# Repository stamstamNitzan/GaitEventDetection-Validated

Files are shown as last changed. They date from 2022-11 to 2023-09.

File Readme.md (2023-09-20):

# Gait Event Detection Device -> Validated

## Background
The gait events detection algorithm is based on angular velocity data from a single gyroscope mounted on the shank. The code was written for ***Arduino Nano 33 BLE Sense***. The developed device is part of a research study on the effect of haptic feedback on walking biomechanics parameters. With the algorithm, we can detect ***heel-strike*** and ***mid-swing events*** with ***high accuracy*** and provide gait event-dependent ***biofeedback***. 

The device was designed to be versatile and can be ***easily modified for other applications*** that could benefit from ***real-time gait event detection***, ***gait event-dependent feedback***, and ***gait data collection***. Angular velocity data can be collected with a nearby phone via BLE. The device is not confined to the lab setting. It can be modulated for other applications by adding sensors and functions, such as surface electromyography for muscle function monitoring, auditory and visual for biofeedback, and exoskeleton control for assistive walking.

We have validated the gait event detection algorithm's accuracy at detecting heel-strike. We have evaluated healthy participants' changes in ankle flexion moment and flexion angle when intermittent vibration is applied to the lower leg.

The accuracy of the gait event detection algorithm was validated against gold standard floor-embedded force plates (model BMS400600, AMTI, MA, USA). We compared the time difference between detecting a heel-strike event by the force plates and the device. The detection of heel-strike events in real-time by the device showed excellent agreement with the force plates at all three speeds (ICC = 1). Our device's mean difference and standard deviation in heel-strike detection are 19 ± 22 ms, and the sampling rate was 100 Hz. 

## Table of Contents
- [Background](#background)
- [Using the code for event-dependent processes and gait analysis](#using-the-code-for-event-dependent-processes-and-gait-analysis)
  * [Controlling the device via the nRF Connect app](#controlling-the-device-via-the-nrf-connect-app) 
  * [Algorithm workflow](#algorithm-workflow)
  * [Modifying the biofeedback](#modifying-the-biofeedback)
- [Device design and electrical diagram](#device-design-and-electrical-diagram)
  * [Electrical diagram](#electrical-diagram)
  * [Gait event detection validation](#gait-event-detection-validation)
  * [Gait dependent biofeedback](#gait-dependent-biofeedback)
- [License](#license)
- [Citation](#citation)
- [Contact](#contact)

## Using the code for event-dependent processes and gait analysis

The algorithm detects two gait events (heel-strike and mid-swing); however, accuracy measurements were done for heel-strike events. Our application was to use heel-strike events detection to activate intermittent vibration during specific parts of the stance phase. The code can be modified to provide any event-based processes that are in the scope of Arduino's abilities. 

We have uploaded three examples to this repository of using the algorithm. You can also find two ways to convert the recorded data from nRF Connect to meaningful angular velocity values. The first option is MATLAB code that does that automatically, and the second option is with Excel. All examples record the gyroscope's data to a buffer that can be sent to the phone at the end of each run. Only the `GaitDetectionOnlyRecordingGyro.ino` example is sending the data in real time.

Here are the examples:
- [GaitDetectionOnlyRecordingGyro.ino](GaitDetectionOnlyRecordingGyro/GaitDetectionOnlyRecordingGyro.ino) – sending gyroscope data to nRF Connect in real-time.
- [GaitDetectionLightOnly.ino](GaitDetectionLightOnly/GaitDetectionLightOnly.ino) – turning on LED on heel-strike events and turning it off on calculated toe-off events.
- [GaitDetectionWithVibration.ino](GaitDetectionWithVibration/GaitDetectionWithVibration.ino) – turning on the first vibration motor at heel-strike and turning on the second motor at about 30% of the gait cycle. Both motors are turned off at toe-off events (about 60% of the gait cycle).
- [DataConversionXMLtoMatlab.m](Post-analysis/DataConversionXMLtoMatlab.m) – import recorded XML files and converts the data to angular velocity meaningful values using MATLAB.
- [GyroDataExcelTutorial.pdf](Post-analysis/GyroDataExcelTutorial.pdf) – you can also use Excel to convert angular velocity to meaningful values. Explanation on how to convert gyro data from XML file to Excel by Omri Yosfan (omri.yy@gmail.com).

### Controlling the device via the nRF Connect app
After uploading the code to the Arduino Nano 33 BLE Sense, the device will be in standby mode, waiting for Bluetooth connection and commands. There are three commands:

`01` – "Reset", reset buffer

`02` – "Record", run the gait detection algorithm, send real-time gyroscope data, and/or provide event-dependent processes (when applicable).

`03` – "Replay", resend gyroscope data.

When sending the command "02", the code will run for the amount of time set by ` #define RECORDING_LENGTH_SECONDS `.

####  Working with the nRF Connect app 

**Step 1:** Download and install the app from your phone app store and give the required permissions. [https://www.nordicsemi.com/Products/Development-tools/nrf-connect-for-mobile](https://www.nordicsemi.com/Products/Development-tools/nrf-connect-for-mobile )

**Step 2:** Open the app and turn on Bluetooth and location access. Click on the scan button and connect to your device (the default is "Nitzan Arduino").

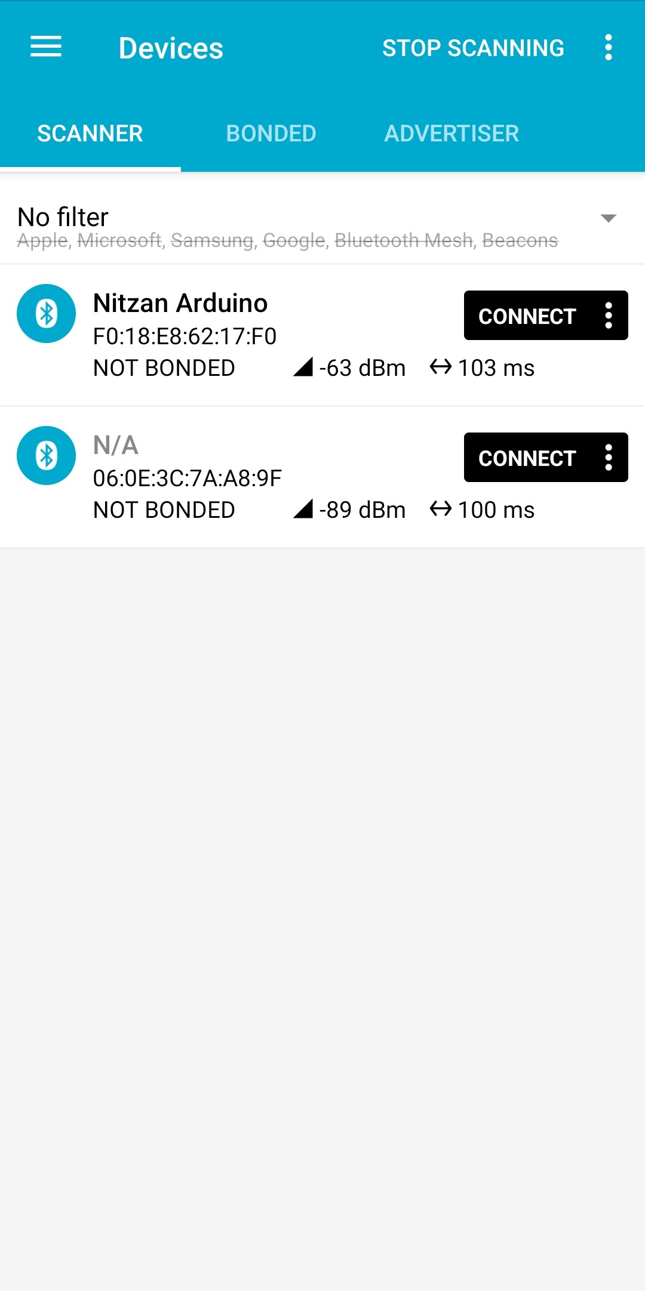
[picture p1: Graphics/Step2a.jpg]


**Step 3:** Press on the three dots next to "SERVER", click on "Request connection priority" and choose "HIGH".

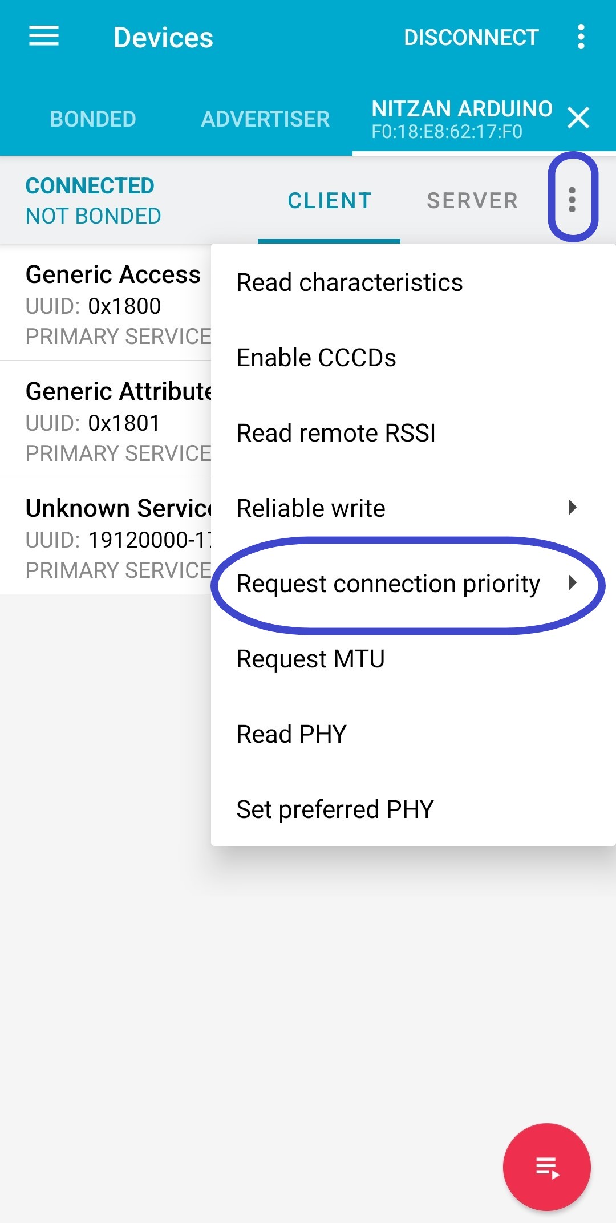
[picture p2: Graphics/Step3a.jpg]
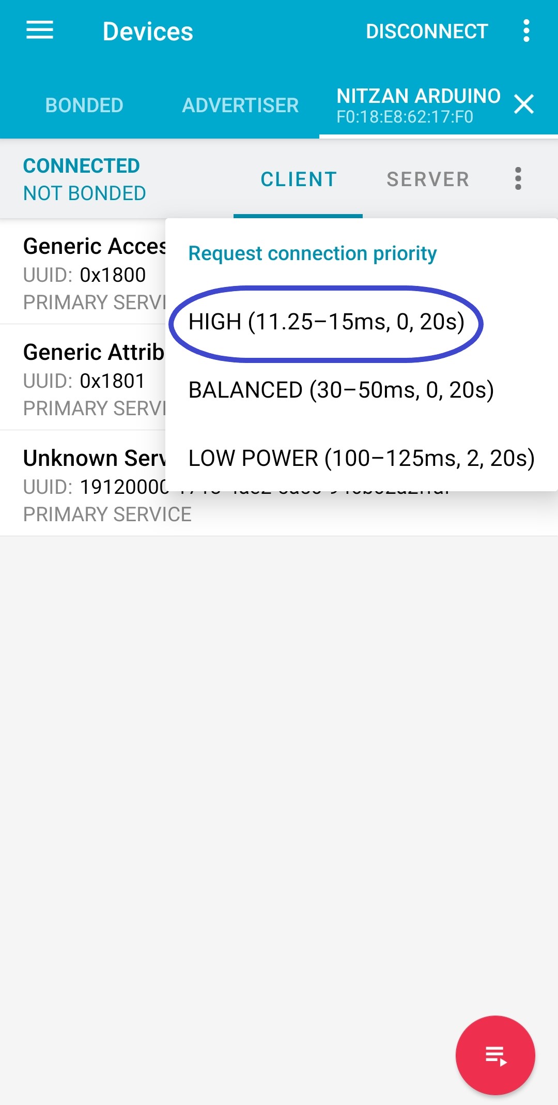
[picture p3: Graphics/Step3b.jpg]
        

**Step 4:** Press on "Unknown Service" and then press on the three arrows pointing down next to "Unknown Characteristic", this will let you receive the data from the Arduino.

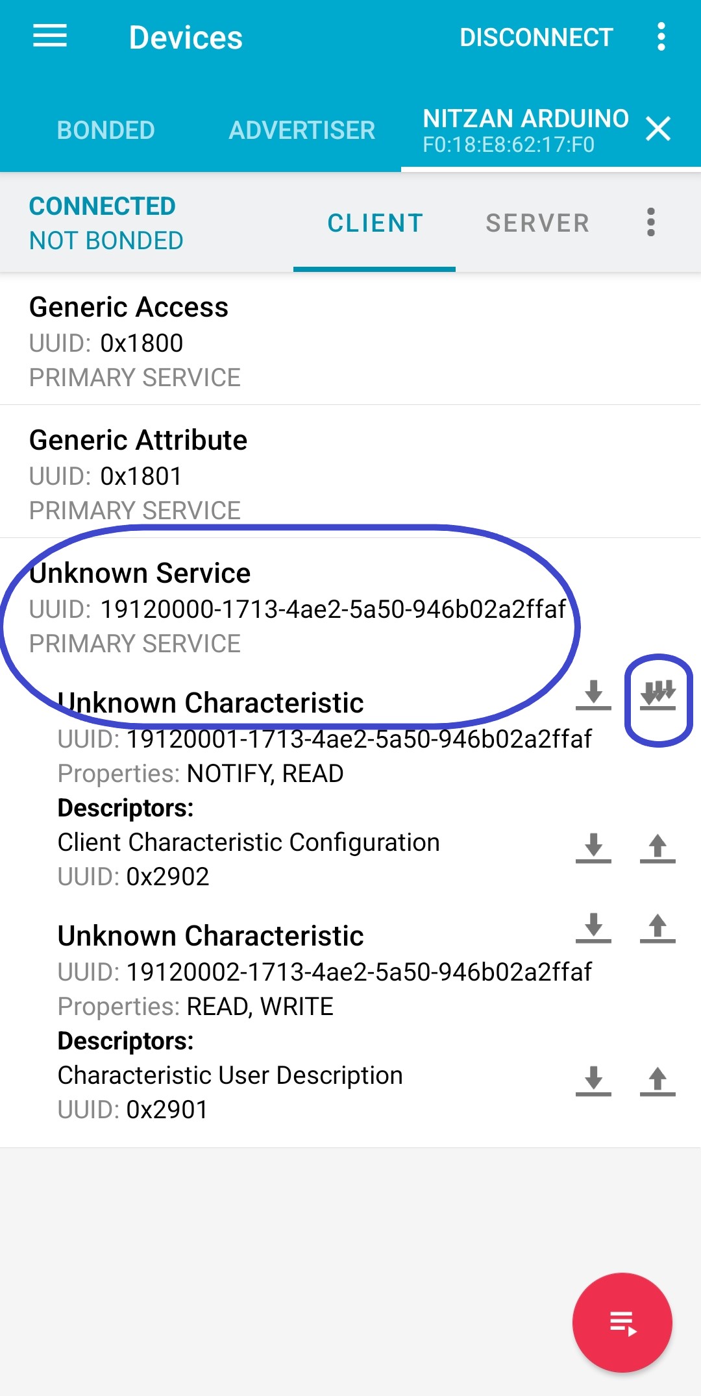
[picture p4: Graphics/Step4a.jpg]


**Step 5:** SENDING COMMANDS. As mentioned above, there are three commands, each with a corresponding number. Press on the middle arrow pointing UP to open the command dialog. Press "SEND" to commit the command.

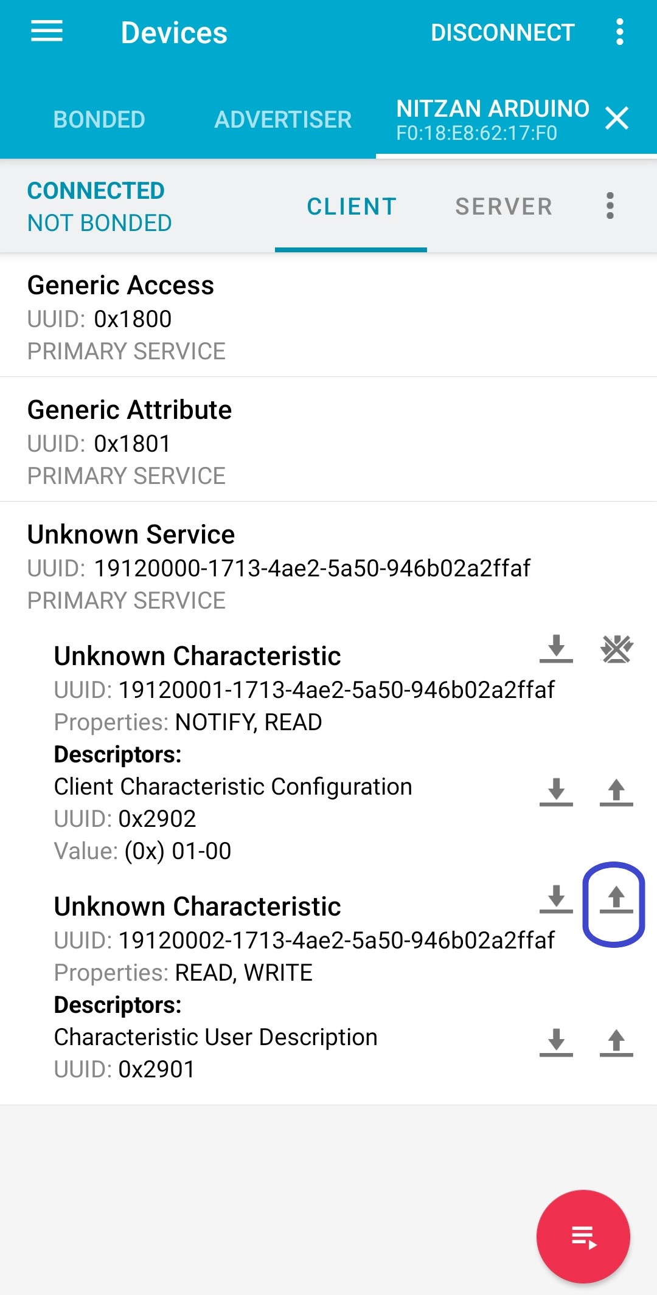
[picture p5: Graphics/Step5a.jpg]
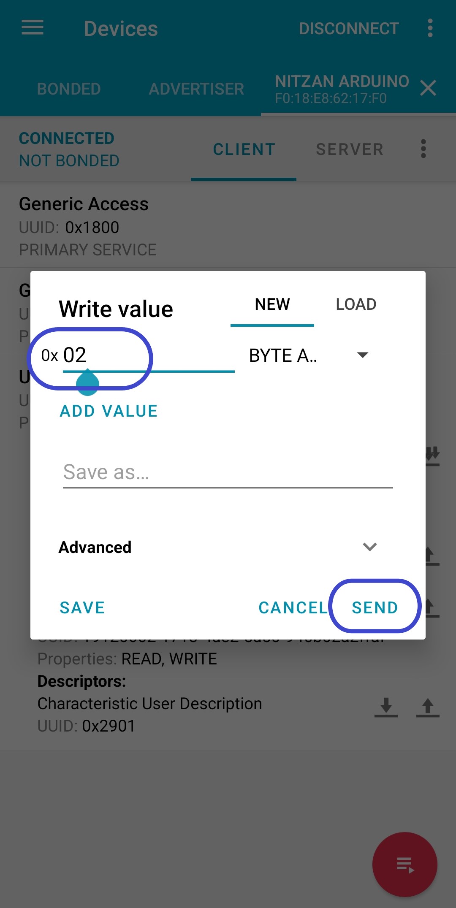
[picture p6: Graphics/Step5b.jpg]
        

**Step 6:** RECORDING THE DATA and saving it. The nRF Connect app receives the angular velocity data in real-time. To record the data, press on the red button and then on the red recording button. To stop the recording, press on the red button with a square inside and give the recording a name. 

*Important*: the three arrows pointing down must be pressed for real-time data streaming.

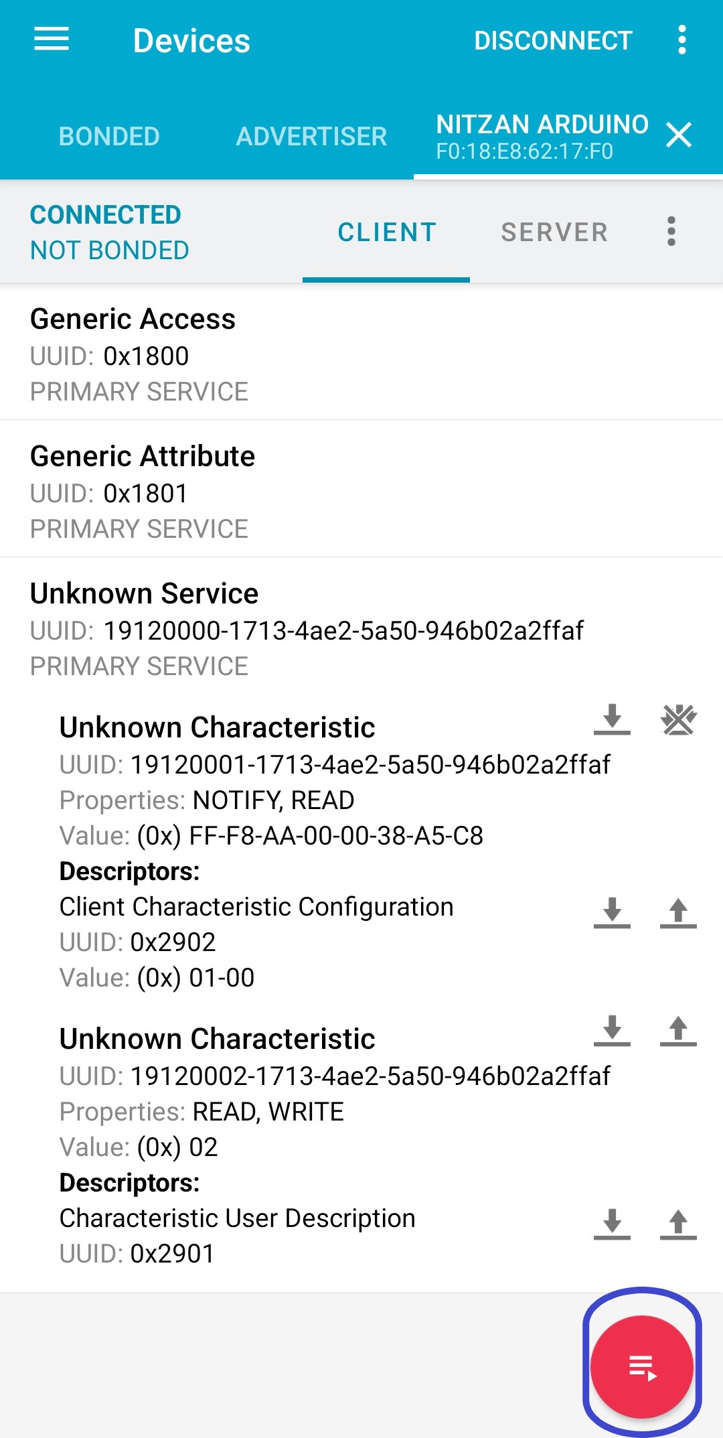
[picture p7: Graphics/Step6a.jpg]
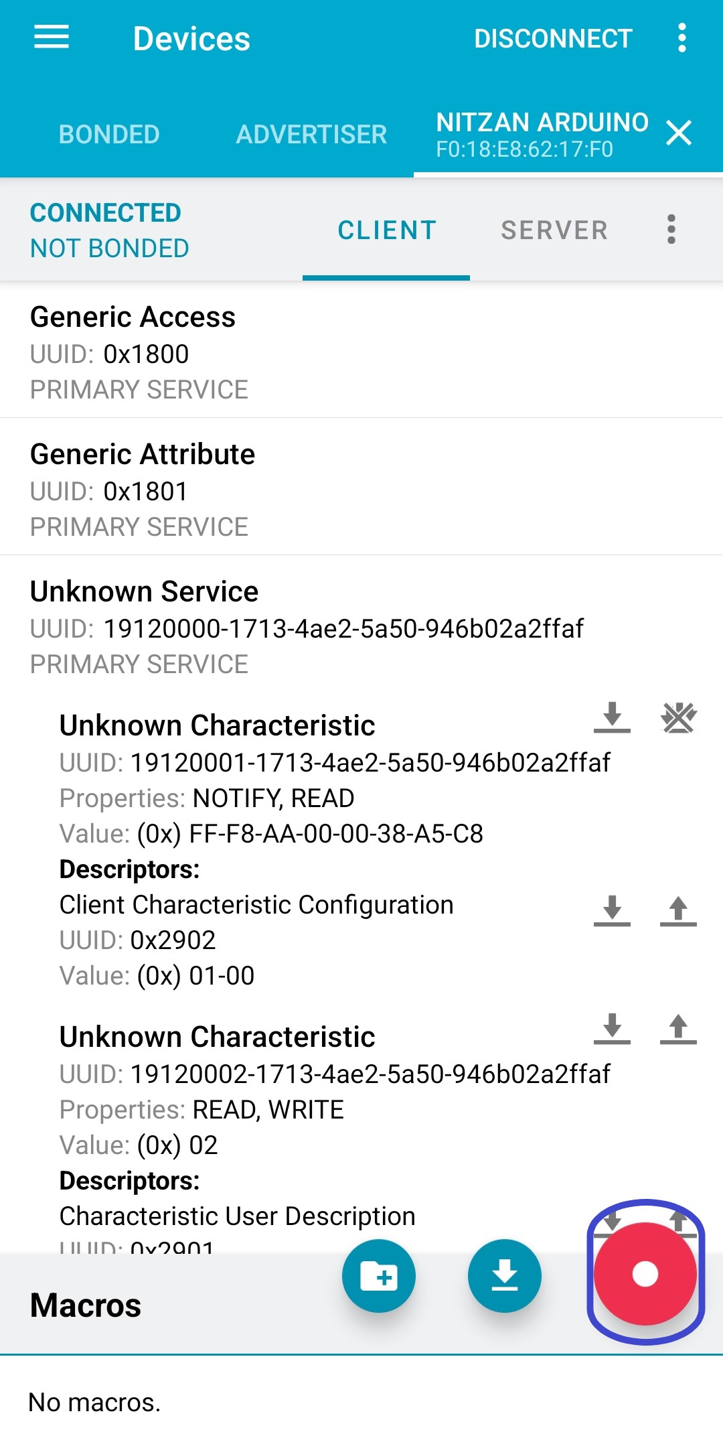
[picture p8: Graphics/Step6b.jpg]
        

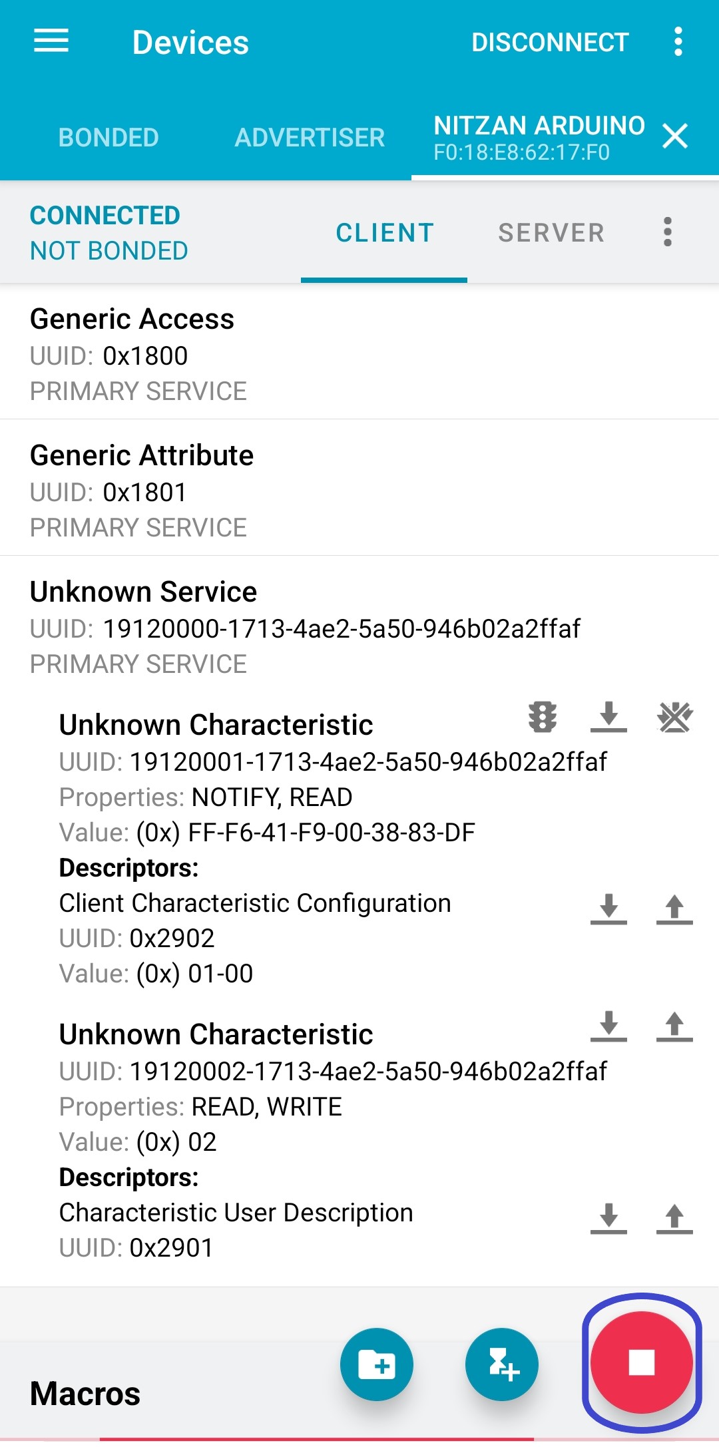
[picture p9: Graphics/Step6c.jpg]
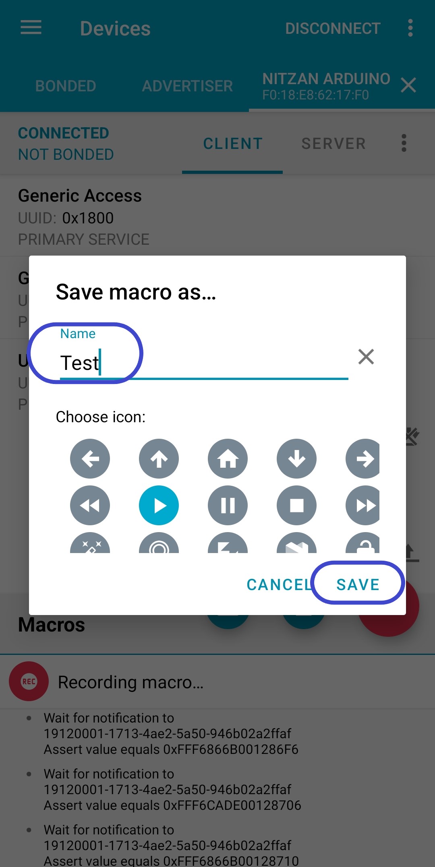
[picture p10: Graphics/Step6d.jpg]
        

**Step 7:** Export the recording to an XML file and save it on your phone for post-processing gait analysis. Post-analysis can be done using the raw data with the MATLAB code or the excel tutorial. You can find a discussion about the raw data import and conversion on the [looking-for-ble-logger-app](https://forum.arduino.cc/t/looking-for-ble-logger-app/870554) Arduino forum.

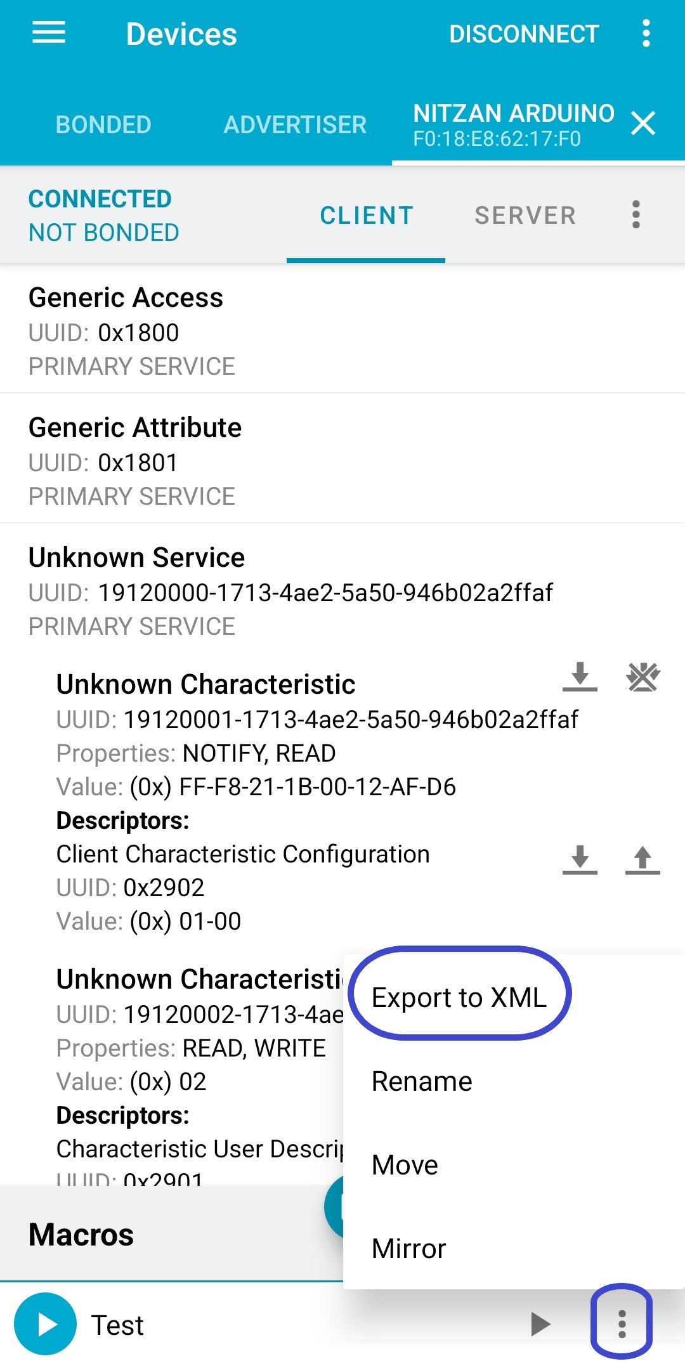
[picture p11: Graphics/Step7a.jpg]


### Algorithm workflow
The algorithm detects two distinct gait events in real-time: mid-swing and heel-strike. These gait events are calculated by unique features of the angular velocity signal, such as the global maxima, zero-crossing, and local negative minima, as described by Fu-Cheng Wang et al (2020)., (Figure 1). We incorporated a patient-specific gait pattern self-correcting adjustment of the mid-swing threshold to prevent false detection of mid-swing events. In every gait cycle, we calculated the user's mid-swing average value using a moving-average function with a window size of three data points of the earlier mid-swing events value. We set the mid-swing threshold value to half the mid-swing average. Gait cycle duration was calculated as the time between the current heel-strike event and the previous one. The toe-off event was calculated as 60% of the gait cycle duration. 
<p align="center">
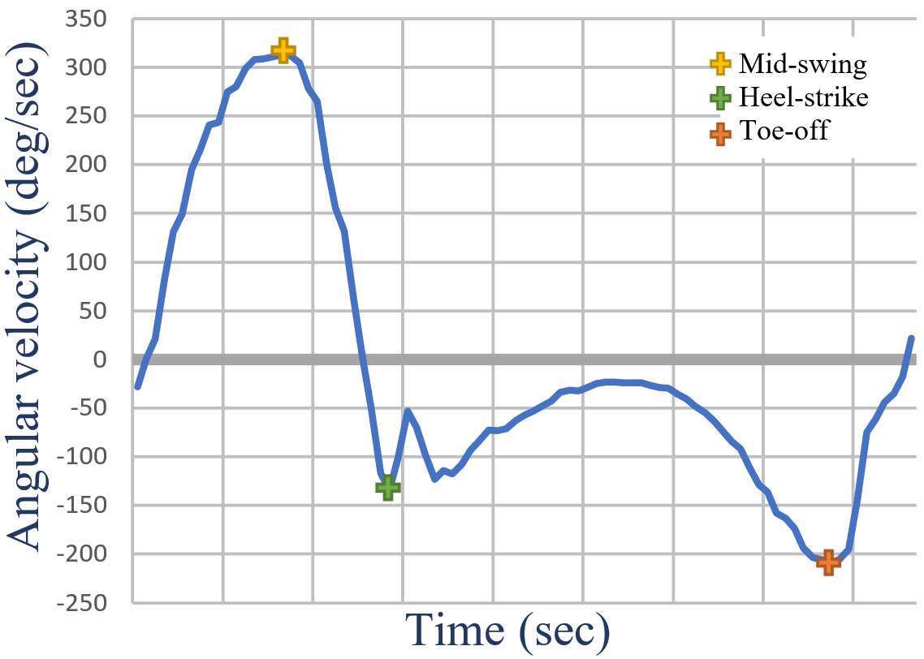
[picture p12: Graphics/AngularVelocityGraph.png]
<br/>
<b>Figure 1. An angular velocity graph is taken from a gyroscope sensor on the shank of a healthy participant. (+): a distinct gait event. From left to right: mid-swing, heel-strike, and toe-off.</b>
</p>

Upon algorithm startup, it establishes the initial gait cycle duration and updates the user-specific mid-swing threshold from the first two steps (three global maximum). Next, the algorithm searches for the first negative minimum after mid-swing, which would be a heel-strike event. In some individuals, there is a positive local maximum after the heel-strike caused by the impact of the heel-strike and shank moment-of-inertia. Therefore, five sample points after a heel-strike event was detected are being ignored to avoid false-positive mid-swing detection. Gait cycle duration and mid-swing values are constantly updated. Suppose the interval between two successive mid-swing events is higher than 1.5 times the average gait cycle duration; then, the algorithm treats it as if the person turned around or stopped and waits for the subsequent step initiation. An algorithm workflow diagram is depicted in Figure 2.
<p align="center">
<br/>
<b>Figure 2. Workflow chart of the algorithm logic of the gait events detection. g(t) is the current gyroscope value, MS_th is the threshold value for searching for mid-swing, SL_t(t) is the current step length time, and SL_avg is the step length average time. A green box represents an input signal, and a trapezoid represents condition statements.</b>
</p>

### Modifying the biofeedback
In examples "GaitDetectionLightOnly.ino" and "GaitDetectionWithVibration.ino", you can find the function `void vibrationTask()`
. To start ***your*** biofeedback, insert the part of your code after `if (readyToVibrate) { `. To stop ***your*** biofeedback, insert your end condition after     
` if (vibrationPhase) { ` .

## Device design and electrical diagram
The enclosures were printed in a 3D printer and STL files are available in the "Enclosures" folder.

### Electrical diagram
Below is an electrical diagram of the device.

<p align="center">
<br/>
<b>Figure 3. Circuit diagram of phase 2, units, and components list.</b>
</p>

### Gait event detection validation
Below are pictures of the gait event detection device, operating a red LED indicator. Example: `GaitDetectionLightOnly.ino`

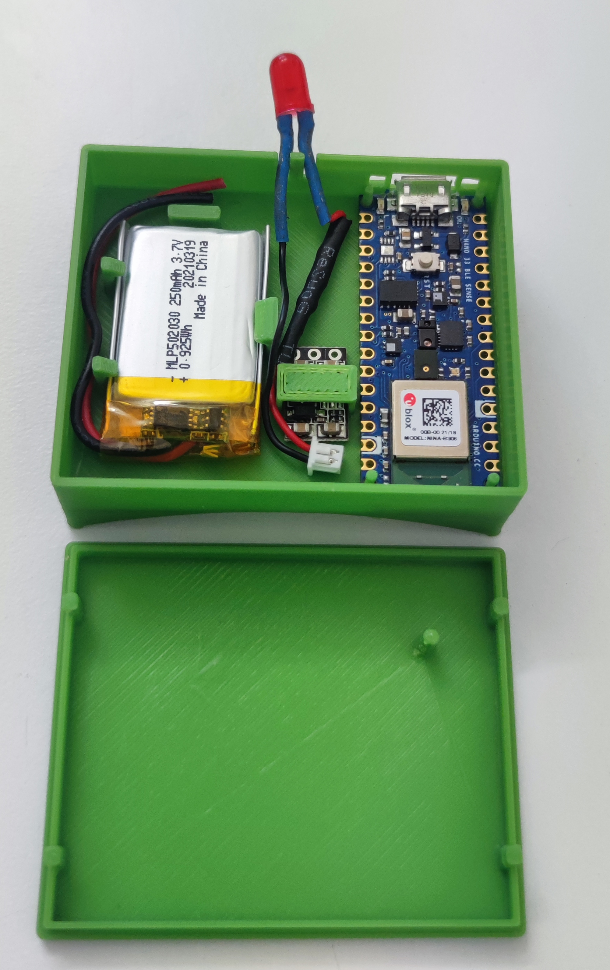
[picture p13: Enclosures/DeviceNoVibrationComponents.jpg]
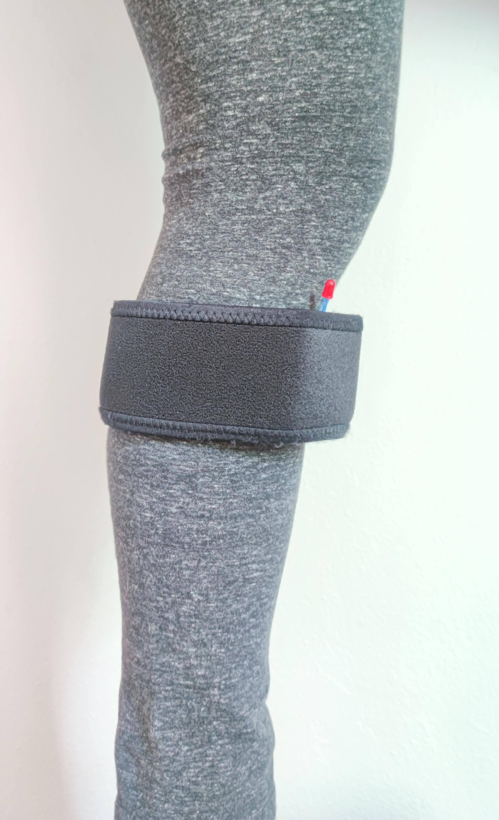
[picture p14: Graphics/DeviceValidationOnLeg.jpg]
        

### Gait dependent biofeedback
Below is the complete device with two vibration motors that provide haptic feedback. Example: `GaitDetectionWithVibration.ino` 

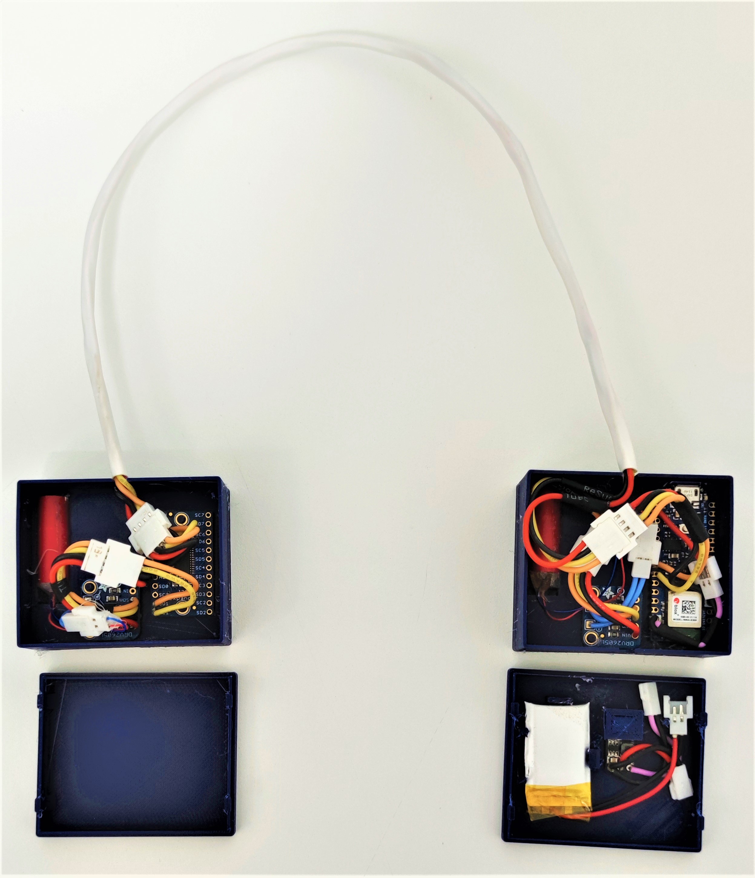
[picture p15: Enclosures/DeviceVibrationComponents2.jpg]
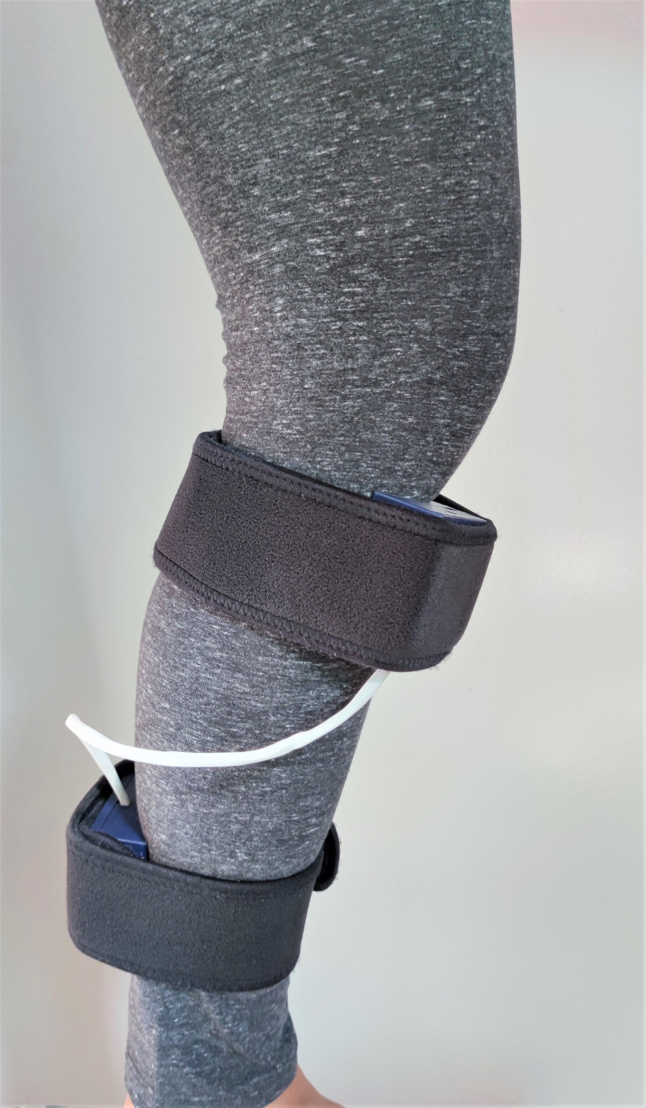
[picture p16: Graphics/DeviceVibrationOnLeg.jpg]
                

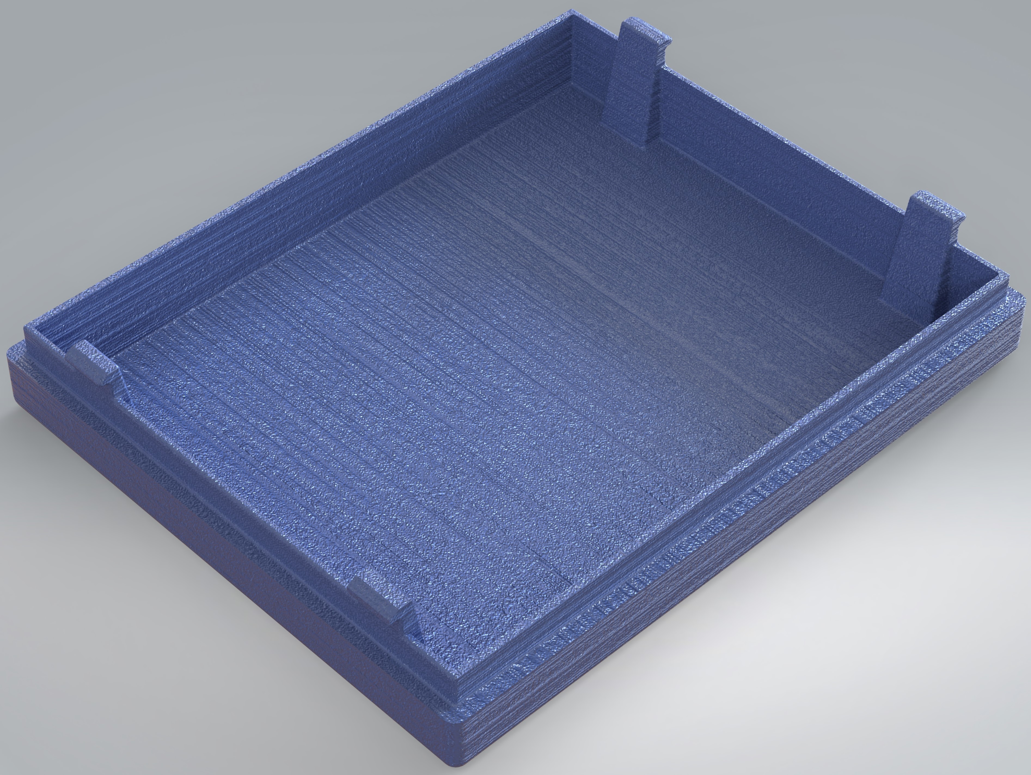
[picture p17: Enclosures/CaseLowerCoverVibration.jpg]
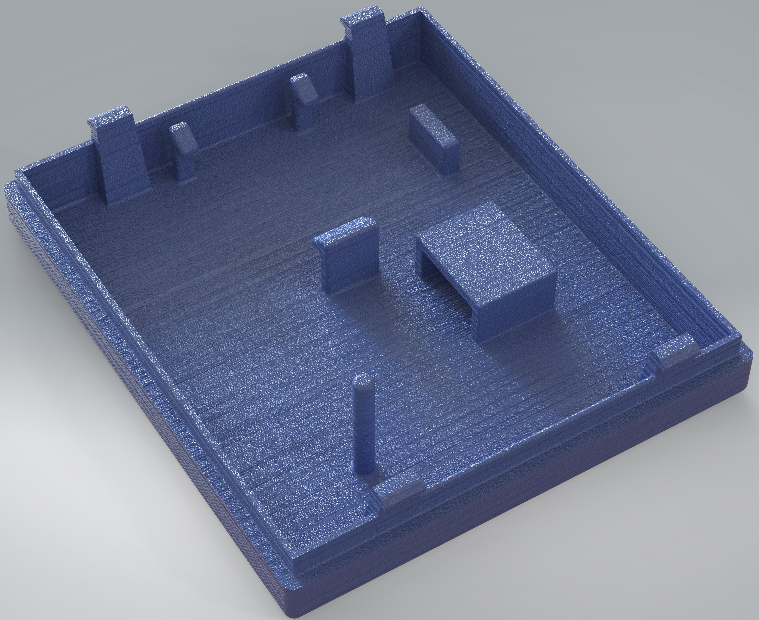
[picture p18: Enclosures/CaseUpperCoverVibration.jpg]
        

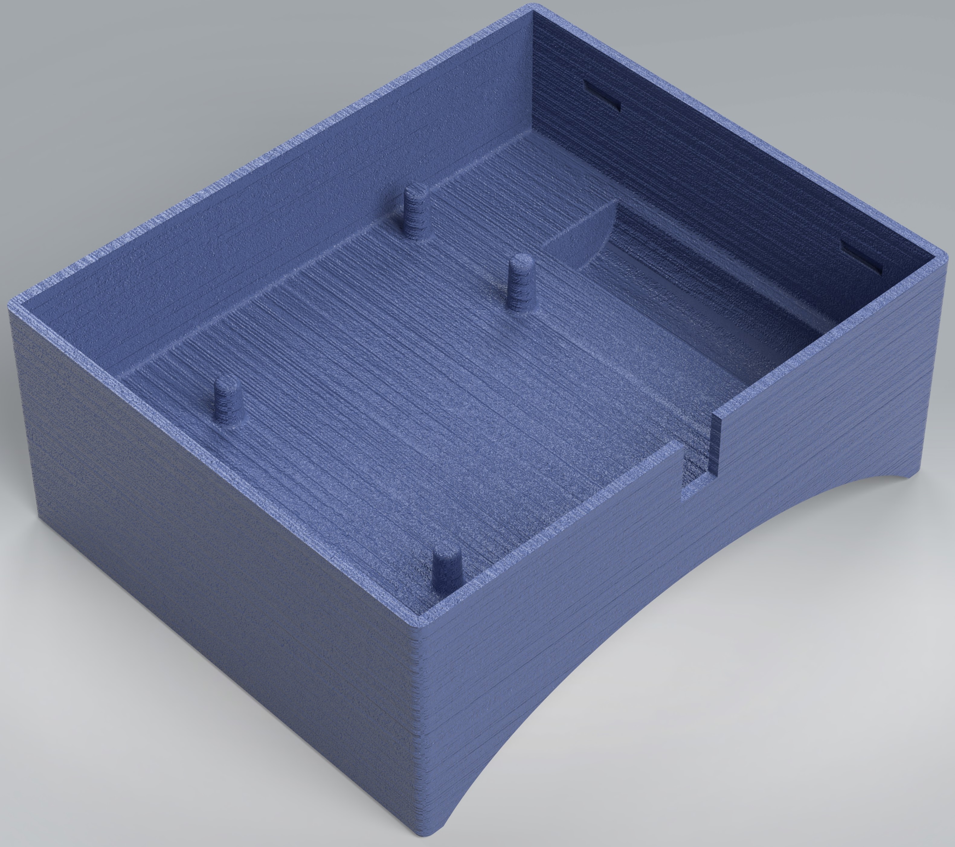
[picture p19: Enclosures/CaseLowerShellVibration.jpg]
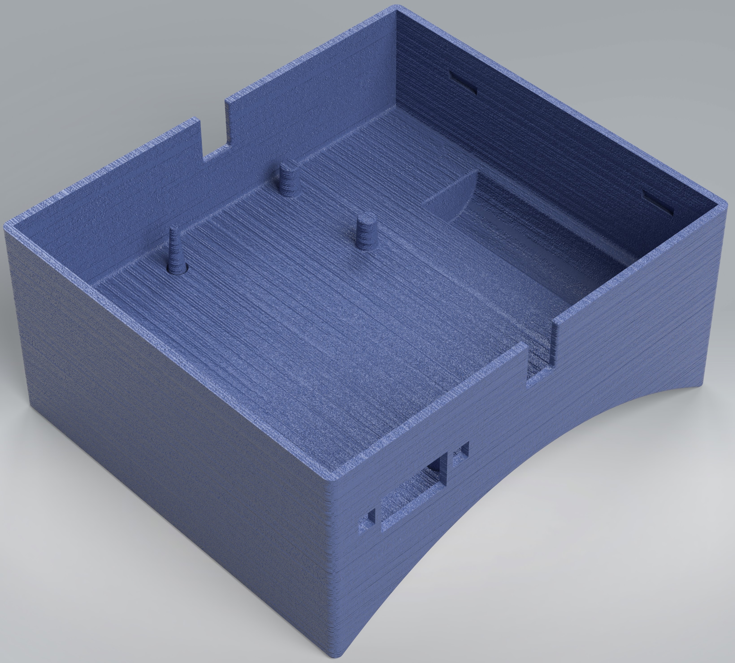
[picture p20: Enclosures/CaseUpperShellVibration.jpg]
        

## License 
Copyright 2022 Nitzan Breitman 

Licensed under the Educational Community License, Version 2.0 (the "License"); you may not use this file except in compliance with the License. 

You may obtain a copy of the License at [https://opensource.org/licenses/ECL-2.0](https://opensource.org/licenses/ECL-2.0)

Unless required by applicable law or agreed to in writing, software distributed under the License is distributed on an "AS IS" BASIS, WITHOUT WARRANTIES OR CONDITIONS OF ANY KIND, either express or implied.

See the License for the specific language governing permissions and limitations under the License.

The Educational Community License version 2.0 ("ECL") consists of the Apache 2.0 license, modified to change the scope of the patent grant in section 3 to be specific to the needs of the education communities using this license. The original Apache 2.0 license can be found at: http://www.apache.org/licenses/LICENSE-2.0

## Citation
Remember to give the appropriate credit to the creators of the work.
N. Breitman, T. Yona and A. G. Fischer, "Gait Event Detection Wearable Device Development and the Effect of Vibration Feedback on Ankle Kinematics and Kinetics," in IEEE Sensors Journal, vol. 23, no. 17, pp. 19052-19059, 1 Sept.1, 2023, doi: 10.1109/JSEN.2023.3294306.

[https://ieeexplore.ieee.org/document/10182391](https://ieeexplore.ieee.org/document/10182391)

## Contact
Nitzan Breitman: :email: [nitzan.breitman@gmail.com](mailto:nitzan.breitman@gmail.com)

LinkedIn: [https://www.linkedin.com/in/nitzan-breitman/](https://www.linkedin.com/in/nitzan-breitman/)

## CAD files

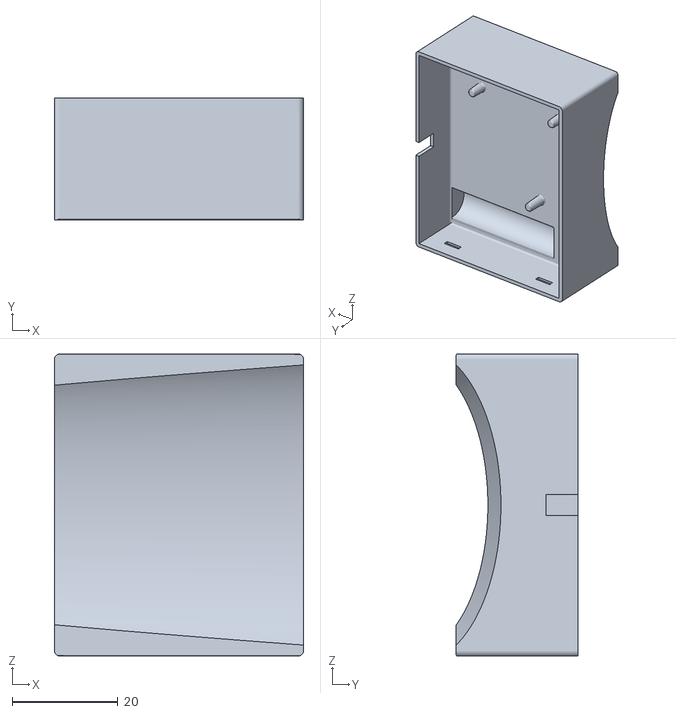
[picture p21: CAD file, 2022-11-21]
Enclosures/CaseLowerShellVibration.STL
47.0 x 22.9 x 57.0

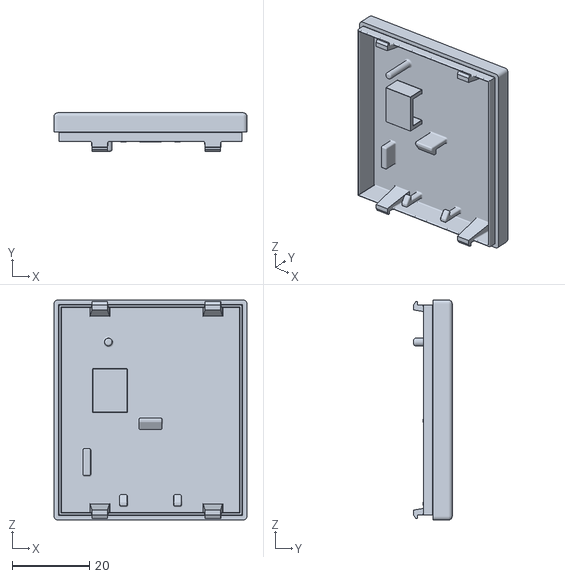
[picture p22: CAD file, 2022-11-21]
Enclosures/CaseUpperCoverVibration.STL
50.0 x 10.0 x 57.0

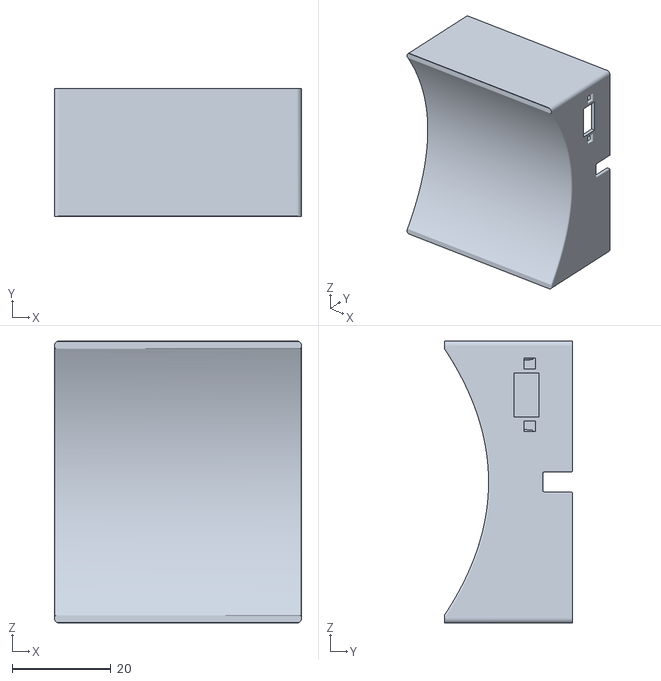
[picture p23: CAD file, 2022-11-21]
Enclosures/CaseUpperShellVibration.STL
50.0 x 25.9 x 57.0

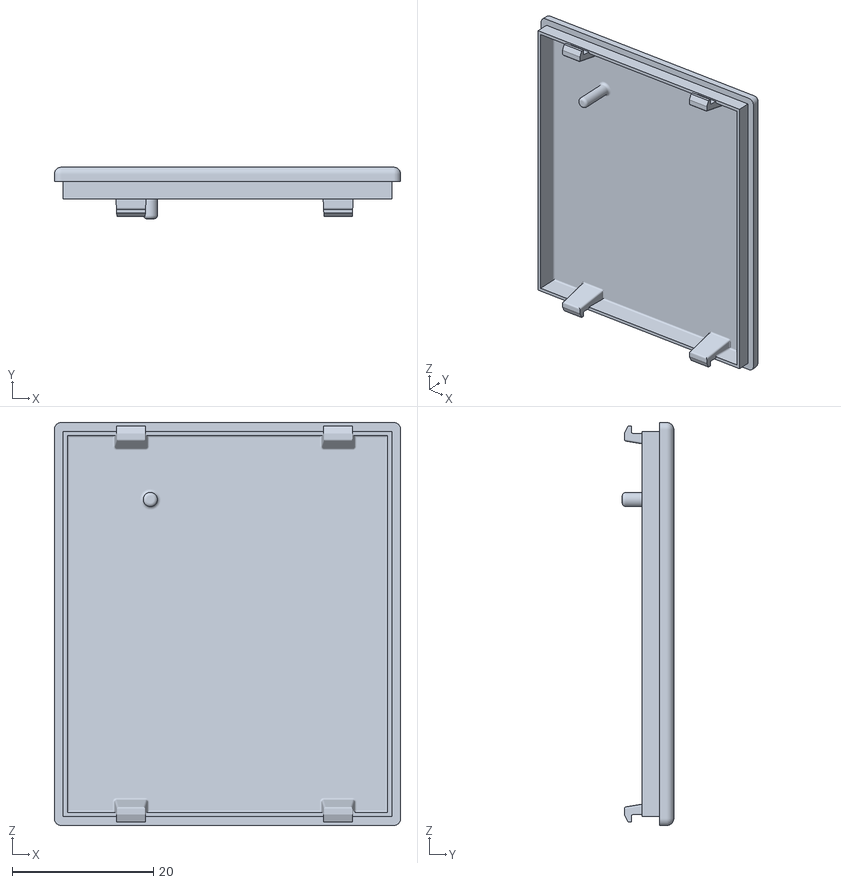
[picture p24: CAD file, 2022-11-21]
Enclosures/CaseUpperCoverNoVibration.STL
49.0 x 7.30 x 57.0

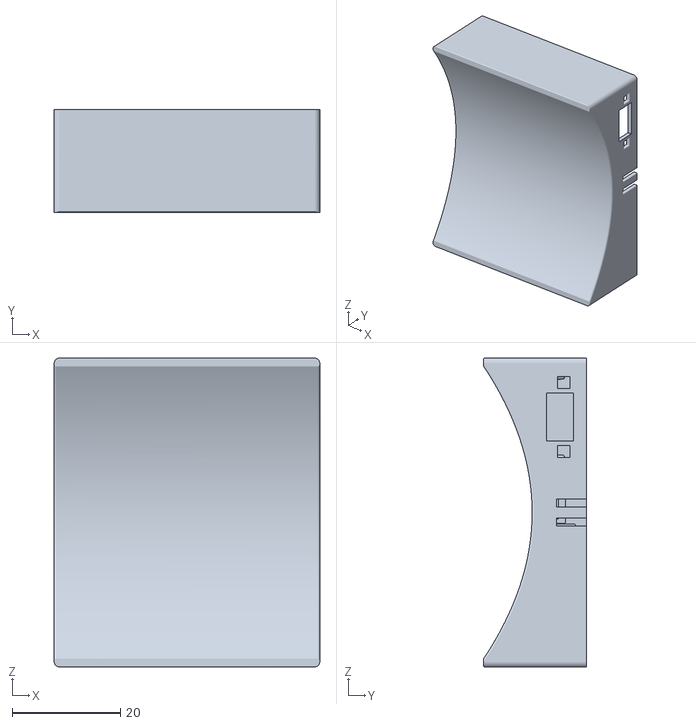
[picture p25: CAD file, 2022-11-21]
Enclosures/CaseUpperShellNoVibration.STL
49.0 x 18.9 x 57.0

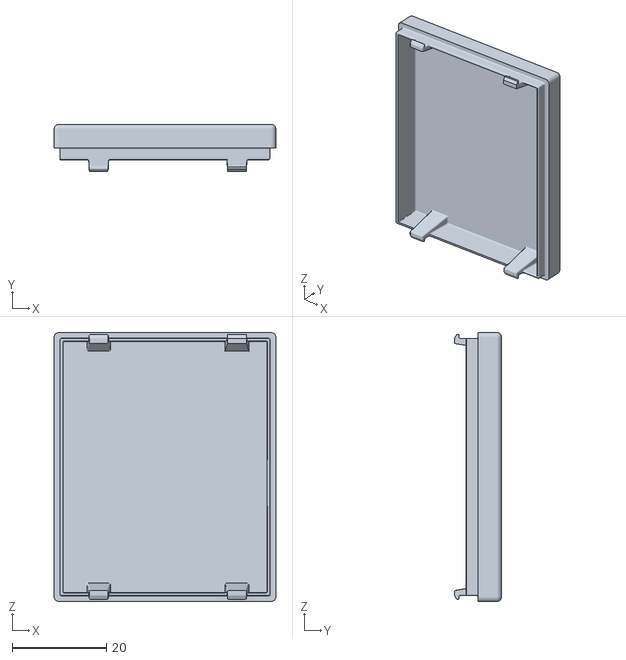
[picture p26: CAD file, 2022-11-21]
Enclosures/CaseLowerCoverVibration.STL
47.0 x 10.0 x 57.0

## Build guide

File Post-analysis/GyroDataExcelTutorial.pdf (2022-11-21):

## Transferring gyro data from XML file to Excel

1. Open Excel and open the XML file
2. Copy data under /wait-for-notification/assert-value/@value
3. Create a new sheet and paste the data into the A column
4. Select the A column, go to Data and select Text to Columns
5. Select fixed width and create a break line after the 8th value (split in half)
6. Make sure to select Text format for both halves of the data
7. Click destination and click on the B column and press finish, data should be split evenly
8. To get millis value:

Select D1 and paste this formula:

= HEX2DEC( RIGHT( A1, 8 ) )

9. Drag the corner down the whole length of the data to fill the remaining cells
10. Go into D1 and subtract the value in the cell in the formula
Example: = HEX2DEC( RIGHT( A1, 8 ) ) - 199234 (whatever value is in E1)
11. Double click D1 corner to change the whole column, now you’re done with millis values.
12. To get gyro values:

In E1 paste this formula:

=IF( HEX2DEC(C1) > HEX2DEC("7FFFFFFF"), HEX2DEC(C1) - HEX2DEC("FFFFFFFF") -1, HEX2DEC(C1) ) /1000000

13. Double click E1 corner and gyro values should fill in
14. Select D and E columns and create a scatter plot
15. Delete outlier rows, resize plot if desired.

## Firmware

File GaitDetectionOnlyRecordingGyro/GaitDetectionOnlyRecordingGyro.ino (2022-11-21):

//Created by Nitzan Breitman and Omri Yosfan. Contact: nitzan.breitman@gmail.com

/*
   This version has the following:

   - To send gyro data on 02
   - When sending 02 from nRF connect, the LED (if connected) turns-on on heel-strike events and turns-off according to VIBRATION_END_PERCENTAGE
   - Recording data to buffer on 02
   - Record data from nRF connect when sending 03
   - To use the heel-strike detection for other applications, then adjust the "vibrationTask" function according to your needs
   - Follow the explanation on our GitHub page to control and record from the phone
   - Licensed under the Educational Community License, Version 2.0 (the "License"); you may not use this file except in compliance with the License. https://opensource.org/licenses/ECL-2.0
   - Copyright 2022 Nitzan Breitman  
*/
#include <MovingAverage.h>    //By Alexandre Hiroyuki
#include <ArduinoBLE.h>       //A general thanks to Klaus_K from the Arduino forum for helping with BLE data transmission
#include <Arduino_LSM9DS1.h>  //By Femme Verbeek 2.0, Calibration per enclosure is advised https://www.youtube.com/watch?v=BLvYFXoP33o
#include <Wire.h>
#include "Adafruit_DRV2605.h"

#define MOTOR_LED D6  //Leave for a time you want to show the visual LED of HS
#define RED 22
#define BLUE 24
#define GREEN 23
#define LED_PWR 25
Adafruit_DRV2605 drv;
MovingAverage<unsigned long> stepLengthAvg(3);  //Makes MovingAvg object with 3 points
MovingAverage<float> peakValueAvg(3);

//Multiplexer
#define TCAADDR 0x70
#define FIRST_DRV 2   //I don't know why but this line has to stay for the two motors to work independently, even when motor 1 is not connected to the multiplexer.02.08.2022
#define SECOND_DRV 1  //Number is channel # on multiplexer

//----------------------------------------------------------------------------------------------------------------------
// User-friendly variable stuff
//----------------------------------------------------------------------------------------------------------------------

#define RECORDING_LENGTH_SECONDS 15           //Length of each trial (seconds)
#define VIBRATION_START_PERCENTAGE_MOTOR1 0   //Percentage of gait cycle when vibration activates (20 = motor starts 20% after HS) motor1= upper motor
#define VIBRATION_START_PERCENTAGE_MOTOR2 30  //MOTOR2=lower motor
#define VIBRATION_END_PERCENTAGE 60           //Percentage of gait cycle when vibration deactivates (60 = motor stops 60% after HS)
#define STEP_LENGTH_THRESHOLD 1.5             //Percentage at which step length won't be added to stepLengthAvg (1.5 = 150%)
int SAMPLES_TO_IGNORE_AFTER_HS = 5;           //Prevents early detection of HS on a spike
float MS_THRESHOLD_PCT_OF_PEAK = 0.5;         //Percentage of moving avg peak value for MS detection threshold
float INITIAL_MS_THRESHOLD = 100;             //Fixed-value threshold for initial two steps

//----------------------------------------------------------------------------------------------------------------------
// BLE UUIDs
//----------------------------------------------------------------------------------------------------------------------

#define BLE_UUID_SENSOR_SERVICE "19120000-1713-4AE2-5A50-946B02A2FFAF"
#define BLE_UUID_SENSOR "19120001-1713-4AE2-5A50-946B02A2FFAF"
#define BLE_UUID_SENSOR_CONTROL "19120002-1713-4AE2-5A50-946B02A2FFAF"
#define BLE_UUID_CHARACTERISTIC_USER_DESCRIPTION "2901"

//----------------------------------------------------------------------------------------------------------------------
// BLE Setup
//----------------------------------------------------------------------------------------------------------------------

typedef struct __attribute__((packed)) {
  uint32_t position;
  uint32_t time;
} sensor_data_t;

typedef union {
  sensor_data_t values;
  uint8_t bytes[sizeof(sensor_data_t)];
} sensor_data_ut;

sensor_data_ut sensorData;

bool sensorDataUpdated = false;
//----- DEVICE NAME -----//
#define BLE_DEVICE_NAME "Nitzan Arduino"
#define BLE_LOCAL_NAME "Nitzan Arduino"

BLEService sensorService(BLE_UUID_SENSOR_SERVICE);
BLECharacteristic sensorCharacteristic(BLE_UUID_SENSOR, BLERead | BLENotify, sizeof(sensor_data_ut));
BLEByteCharacteristic controlCharacteristic(BLE_UUID_SENSOR_CONTROL, BLERead | BLEWrite);

BLEDescriptor controlDescriptor(BLE_UUID_CHARACTERISTIC_USER_DESCRIPTION, "CMD:01-RESET,02-RECORD,03-REPLAY");

//----------------------------------------------------------------------------------------------------------------------
// APP & I/O
//----------------------------------------------------------------------------------------------------------------------

// Reversing Byte order allows uint32_t data to be converted in Excel with HEX2DEC function OR MATLAB code
#define REVERSE_BYTE_ORDER

#define DATA_BUFFER_SIZE (RECORDING_LENGTH_SECONDS * 100)  // 20 sec X 100 Hz    Changes buffer size

enum BUFER_STATE_TYPE { BUFFER_STATE_READY,
                        BUFFER_STATE_RECORD,
                        BUFFER_STATE_REPLAY,
                        BUFFER_STATE_FULL
};

typedef struct __attribute__((packed)) {
  sensor_data_t values[DATA_BUFFER_SIZE];
  uint32_t index;
  uint32_t state = BUFFER_STATE_READY;
} sensor_buffer_t;

sensor_buffer_t dataBuffer;
bool sensorActive = false;


#define BLE_LED_PIN LED_BUILTIN
#define BUFFER_LED_PIN LED_PWR
#define SENSOR_PIN A0


//----------------------------------------------------------------------------------------------------------------------
// Setup
//----------------------------------------------------------------------------------------------------------------------

void setup() {



  Wire.begin();
  Wire.setClock(400000);
  // Serial.begin(115200);
  pinMode(BLE_LED_PIN, OUTPUT);
  digitalWrite(BLE_LED_PIN, LOW);
  pinMode(BUFFER_LED_PIN, OUTPUT);
  digitalWrite(BUFFER_LED_PIN, LOW);
  pinMode(MOTOR_LED, OUTPUT);

  // Initialize and Setup IMU
  if (!IMU.begin()) {  //Serial.println("Failed to initialize IMU!");
    while (1) {
      digitalWrite(RED, HIGH);
      delay(300);
      digitalWrite(RED, LOW);
      delay(300);
      digitalWrite(RED, HIGH);
      delay(80);
      digitalWrite(RED, LOW);
      delay(80);
      digitalWrite(RED, HIGH);
      delay(80);
      digitalWrite(RED, LOW);
      delay(300);
    }
  }

  // Accelerometer code UPDATED 25.01.2022 to the enclosure with haptic driver, motor, and battery
  IMU.setAccelFS(2);
  IMU.setAccelODR(4);
  IMU.setAccelOffset(-0.020568, -0.017173, -0.021025);
  IMU.setAccelSlope(1.001473, 0.994344, 1.008665);

  // Gyroscope code
  IMU.setGyroFS(1);
  IMU.setGyroODR(4);
  IMU.setGyroOffset(0.778946, -0.252731, -0.057968);
  IMU.setGyroSlope(1.186009, 1.148361, 1.121111);

  // Magnetometer code
  IMU.setMagnetFS(0);
  IMU.setMagnetODR(8);
  IMU.setMagnetOffset(-35.944824, -79.736938, 13.367920);
  IMU.setMagnetSlope(1.197732, 1.230049, 1.217827);

  IMU.gyroUnit = DEGREEPERSECOND;


  if (!setupBleMode()) {
    //Serial.println( "Failed to initialize BLE!" );
    while (1) {
      digitalWrite(RED, LOW);
      delay(200);
      digitalWrite(RED, HIGH);
      delay(200);
      digitalWrite(BLUE, LOW);
      delay(200);
      digitalWrite(BLUE, HIGH);
      delay(200);
      digitalWrite(RED, LOW);
      delay(200);
      digitalWrite(RED, HIGH);
      delay(200);
    }
  } else {
    //Serial.println( "BLE initialized. Waiting for clients to connect." );
    digitalWrite(GREEN, LOW);
    delay(500);
    digitalWrite(GREEN, HIGH);
    digitalWrite(BLUE, LOW);
    delay(500);
    digitalWrite(BLUE, HIGH);
  }
}

//----------------------------------------------------------------------------------------------------------------------
// Variable Declarations
//----------------------------------------------------------------------------------------------------------------------

//For HS Detection HS=heel-strike
float preVal = 0;
float curVal = 0;

//Gait phase markers
bool MSDetected = false;
bool ZeroCrossP2N = false;  //Crossing from Positive sign to Negative
bool HSDetected = false;
bool firstGyro = true;
unsigned long previousMillis = 0;

//For timing considerations
bool firstHS = true;
bool secondHS = true;
unsigned long firstMillis;
unsigned long newMillis;
unsigned long oldMillis;

//Vibration Task
bool readyToVibrate = false;
bool vibrationPhase = false;
unsigned long currVibeMillis;
unsigned long prevVibeMillis;

// HS detection
unsigned long currDetectMillis;
unsigned long prevDetectMillis;
int sampleCounter = 0;

//MS detection MS=mid-swing
float MS_THRESHOLD = INITIAL_MS_THRESHOLD;  //Minimum value that only above it a mid-swing might be detected. It prevents false positive
float peakValue;
bool checkForPeak = true;
bool setMSThreshold = false;


//For moving average
static int AVG_ARRAY_LENGTH = 3;
unsigned long stepLengthAverage = 0;

//----------------------------------------------------------------------------------------------------------------------
//  Loop
//----------------------------------------------------------------------------------------------------------------------

void loop() {
  bleTask();
  sensorTask();
  sendDataTask(RECORDING_LENGTH_SECONDS);  //UPDATE13/12/2021:This task is relevant only when we want to resend the data AKA REPLAY.
  vibrationTask();
}

//----------------------------------------------------------------------------------------------------------------------
//  BLE Task
//----------------------------------------------------------------------------------------------------------------------

void bleTask() {
  const uint32_t BLE_UPDATE_INTERVAL = 10;
  static uint32_t previousMillis = 0;

  uint32_t currentMillis = millis();
  if (currentMillis - previousMillis >= BLE_UPDATE_INTERVAL) {
    previousMillis = currentMillis;
    BLE.poll();
  }

  if (sensorDataUpdated) {
    sensorDataUpdated = false;
    sensorCharacteristic.writeValue(sensorData.bytes, sizeof sensorData.bytes);
  }
}

enum CMD_TYPE { CMD_RESET_BUFFER = 1,
                CMD_RECORD,
                CMD_REPLAY
                //                CMD_DISCOPARTY #Respect Omri, NB
};


void controlCharacteristicWrittenHandler(BLEDevice central, BLECharacteristic bleCharacteristic) {
  //Serial.print( "BLE characteristic written. UUID: " );
  //Serial.println( bleCharacteristic.uuid() );

  uint8_t cmd;
  if (bleCharacteristic.uuid() == (const char*)BLE_UUID_SENSOR_CONTROL) {
    bleCharacteristic.readValue(cmd);
    ////Serial.print( " CMD: " );
    ////Serial.println( cmd, HEX );
    switch (cmd) {
      case CMD_RESET_BUFFER:
        dataBuffer.index = 0;
        dataBuffer.state = BUFFER_STATE_READY;
        digitalWrite(BUFFER_LED_PIN, LOW);
        ////Serial.println( " Reset" );
        break;
      case CMD_RECORD:
        dataBuffer.index = 0;
        dataBuffer.state = BUFFER_STATE_RECORD;
        digitalWrite(BUFFER_LED_PIN, LOW);
        sensorActive = true;
        ////Serial.println( " Record" );
        firstHS = true;
        secondHS = true;
        break;
      case CMD_REPLAY:
        dataBuffer.index = 0;
        dataBuffer.state = BUFFER_STATE_REPLAY;
        digitalWrite(BUFFER_LED_PIN, LOW);
        sensorActive = false;
        ////Serial.println( " Replay" );
        break;

      default:
        //Serial.println( " unknown" );
        break;
    }
  }
}
//----------------------------------------------------------------------------------------------------------------------
//  Sensor Task
//----------------------------------------------------------------------------------------------------------------------
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
